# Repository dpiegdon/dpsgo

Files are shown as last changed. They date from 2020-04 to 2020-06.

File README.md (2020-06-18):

<!-- vim: tw=72 fo+=a
-->

DPSGO
=====

David's Pretty Satisfactory Gps-disciplined Oscillator

GPS disciplined oscillator
==========================

Accurate frequency reference for measurement equipment.

A 10MHz OCXO is tuned to a timing signal of a GPS, e.g. the 1PPS output.
A frequency syntheziser then generates different signals from this
reference as needed/configured by the user.

Development status
------------------

Currently I am working on the firmware for V1 of the PCB. During that I
found multiple issues with PCB-V1 (<a
href="https://github.com/dpiegdon/dpsgo/blob/master/pcb/export/PCB-v1.pdf">Schematic</a>)
which hopefully culminate in another revision of the PCB, and then the
firmware. See <a
href="https://github.com/dpiegdon/dpsgo/blob/master/pcb/export/PCB-v1.ERRATA">PCB-V1
ERRATA</a>.

I.e.: usable, but only as a prototype development platform for V2.

The main control loop (OCXO -> frequency comparison -> DAC) works and
the OCXO can be tuned to the GPS signal within 1PPB or better.

The chosen *tiny* FPGA is too small to hold all the logic that was
designated for it. Most LEDs are connected to it and cannot be addressed
because of that. Currently also the rotary encoder and buttons are
connected to it and are usable, but may be removed to have more logic
for frequency adjustment. In PCB-V2 I will likely move the UI to the
microcontroller, or pick a slightly larger FPGA, e.g. the HX1K.

System components PCB-V1
------------------------

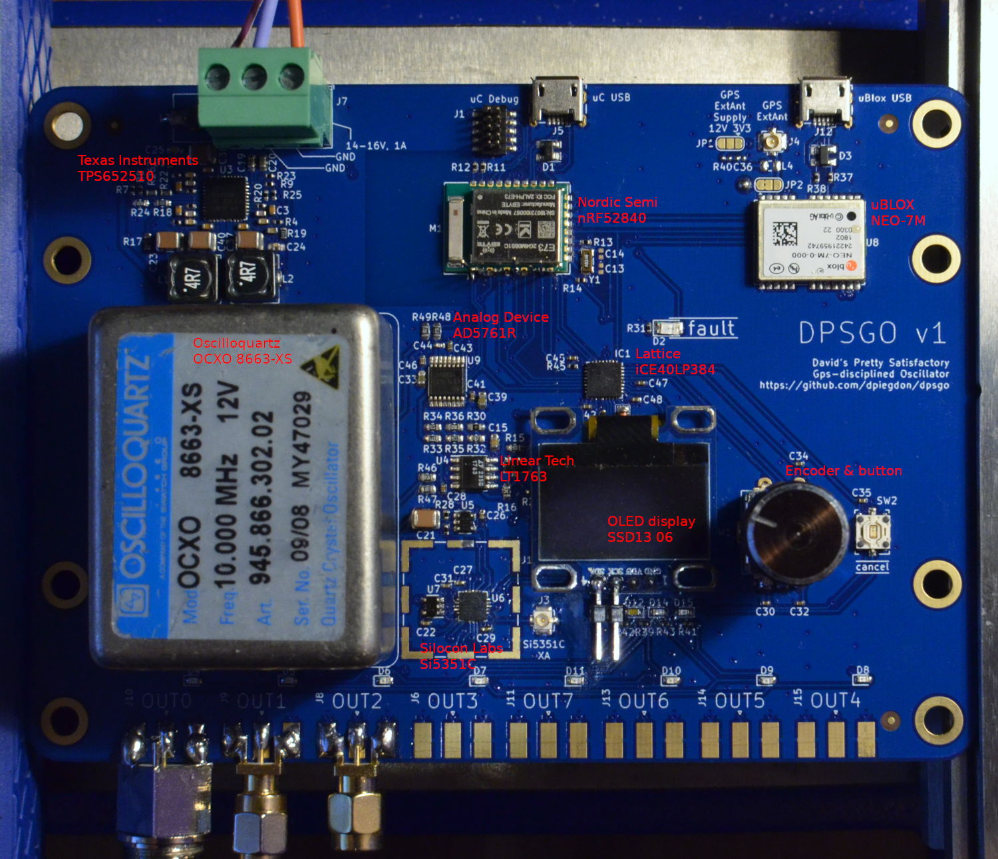
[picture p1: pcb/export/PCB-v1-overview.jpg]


<a
href="https://github.com/dpiegdon/dpsgo/blob/master/pcb/export/PCB-v1.pdf">Schematic.</a>

OCXO: refurbished 8663-XS with 10MHz output

DAC: AD5761R 16bit high quality low speed DAC with internal reference,
generates tuning signal for OCXO

GPS: uBlox NEO 7M module with 1PPS output

VCXO: Si5351-C frequency generator for programmable output frequencies

 * CLK0: 90MHz as input for frequency comparison in the FPGA (for
   automatic tuning)

 * CLK1: 10MHz reference output signal

 * other programmable outputs (currently disabled)

FPGA: Lattice LP384: measures difference between the generated reference
output and the GPS reference signal. That information is used to
calculate the tuning voltage for the OCXO.

uC: nRF52840 as system- and display-controller

Power input: 14-16V

PMIC: TPS652510 PMIC generating three rails of:

 * 12V: OCXO

 * 3.3V: digital logic

 * 1.2V: FPGA core voltage

Additional LDO for:

 * 10V: DAC output rail (from 12V rail)

Temperature sensors: MCP9808 under OCXO and on bottom-side of PMIC (not
visible in photo).

User interface:

 * SSD1306

 * Rotary encoder and buttons (via FPGA)

 * LEDs (currently not addressalbe as FPGA cannot hold more logic)

Interfaces:

 * USB to both GPS receiver and microcontroller

 * potentially Bluetooth or 802.11.5 to microcontroller

 * JTAG/SWD to microcontroller

External references
-------------------

A list of some hobby GPSDO designs:
https://attila.kinali.ch/blog/2016/02/07/gps-disciplined-oscillator

A GPSDO with rubidium standard:
http://www.medpants.com/my-reeds/itemlist/category/28-electronics

Alternative OCXO tuning schematic:
https://gerrysweeney.com/wp-content/uploads/2013/10/OCXO-Rev-1F.png

"bt7tbl" GPSDO that can be bought on the internets:
https://www.eevblog.com/forum/testgear/bg7tbl-gpsdo-master-reference/

Single-chip GPSDO control loop GPSDO:
https://www.analog.com/media/en/technical-documentation/application-notes/AN-1002.pdf

"OpenPPS" GPSDO project:
http://www.rocketmanrc.com/openpps.html

"Themis" GPSDO from HPSDR:
http://openhpsdr.org/wiki/index.php?title=GPSTCXO

GPSDO by dfannin:
https://github.com/dfannin/gpsdo

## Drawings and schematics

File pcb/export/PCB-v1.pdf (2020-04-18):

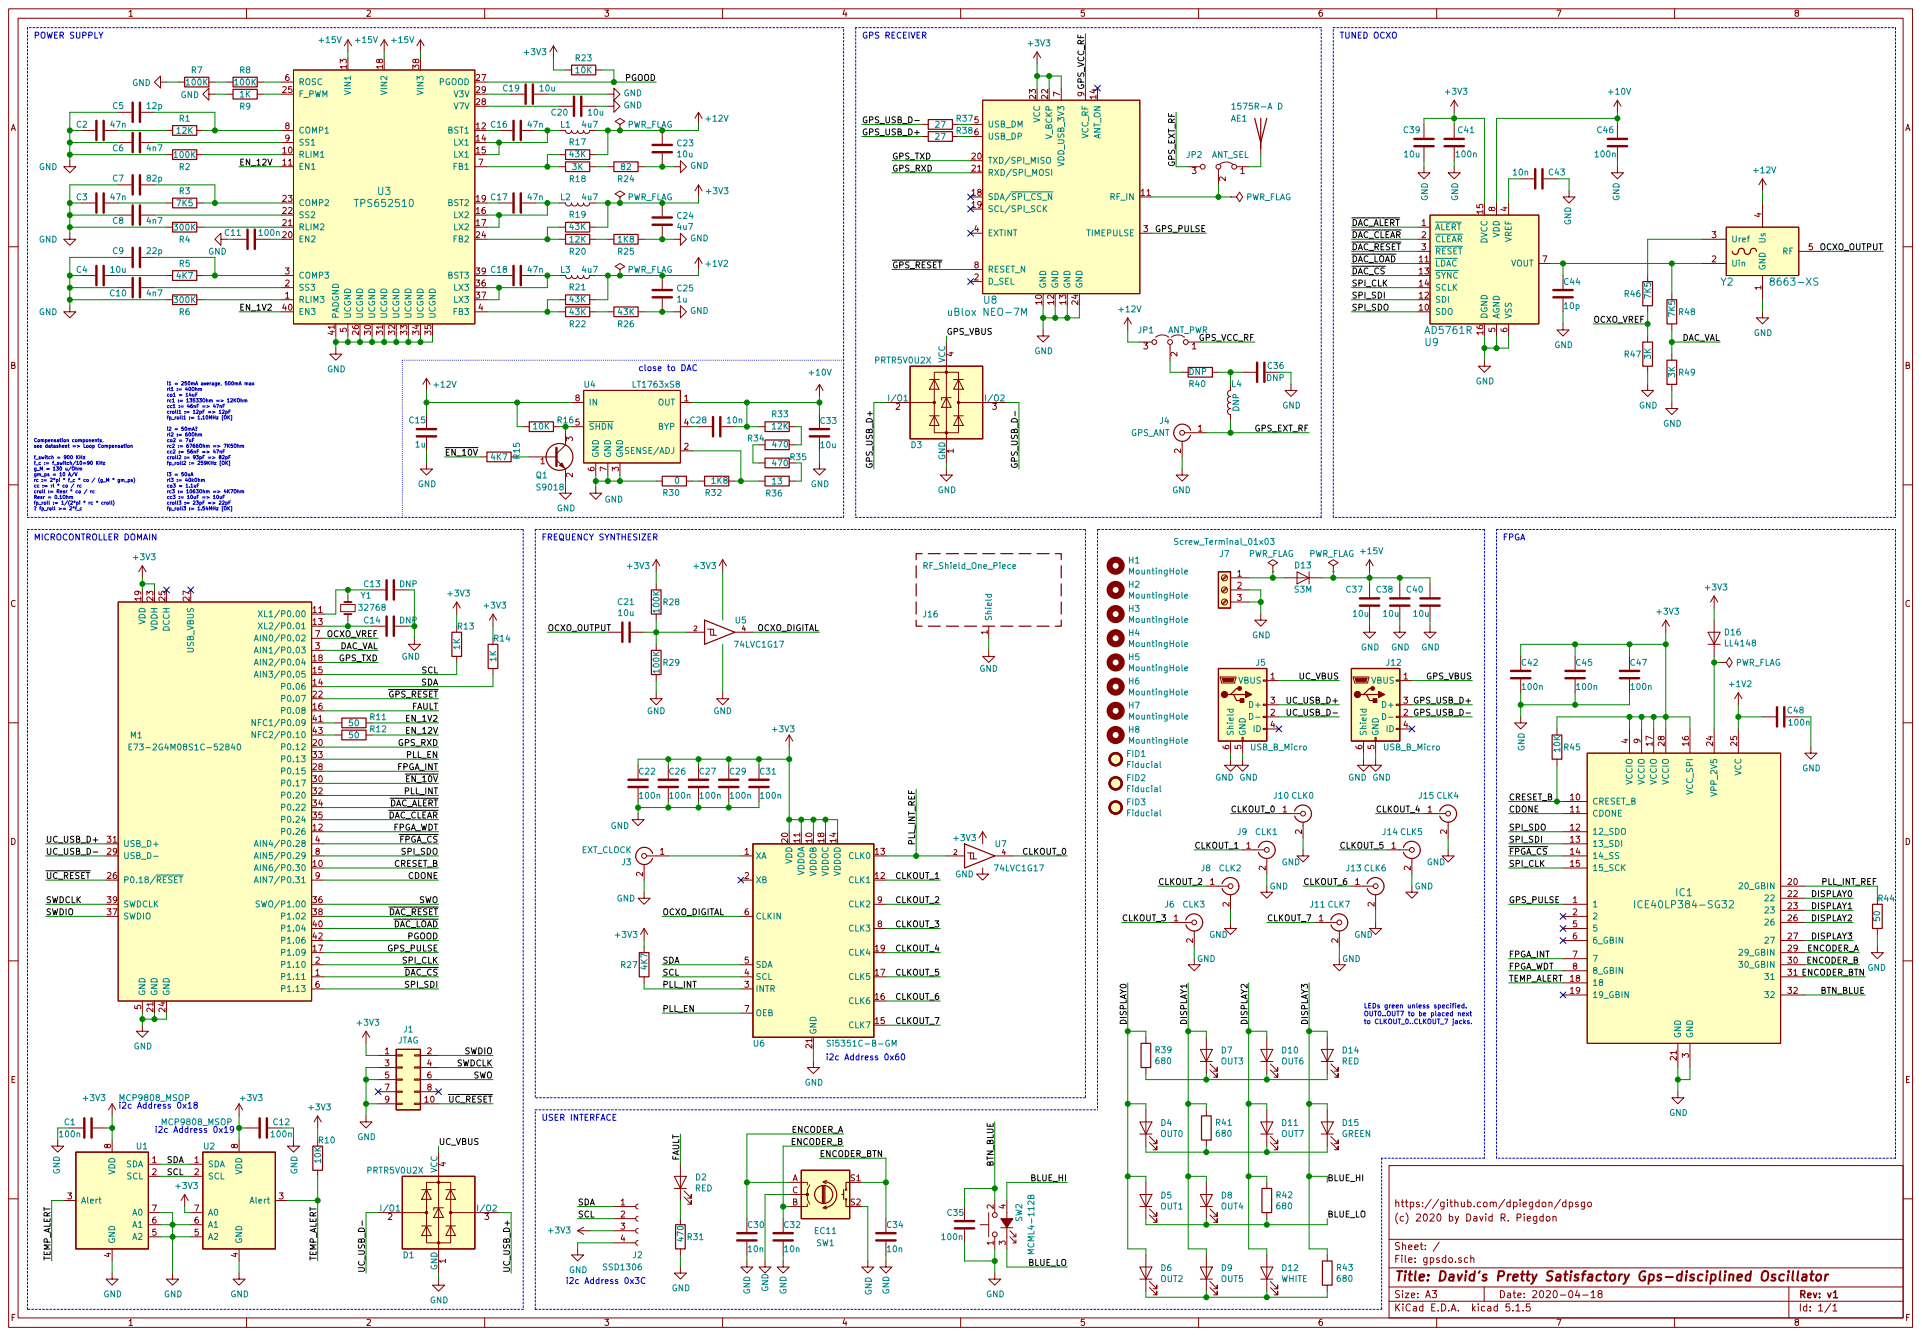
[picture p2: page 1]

Compensation components, see datasheet => Loop Compensation

croll := Resr * co / rc Resr = 0.1Ohm

FID3 Fiducial FID2 Fiducial FID1 Fiducial GNDShield

BLUE_HI LEDs green unless specified. OUT0..OUT7 to be placed next

https://github.com/dpiegdon/dpsgo
File: gpsdo.sch Sheet: / (c) 2020 by David R. Piegdon

Id: 1/1 Title: David's Pretty Satisfactory Gps-disciplined Oscillator

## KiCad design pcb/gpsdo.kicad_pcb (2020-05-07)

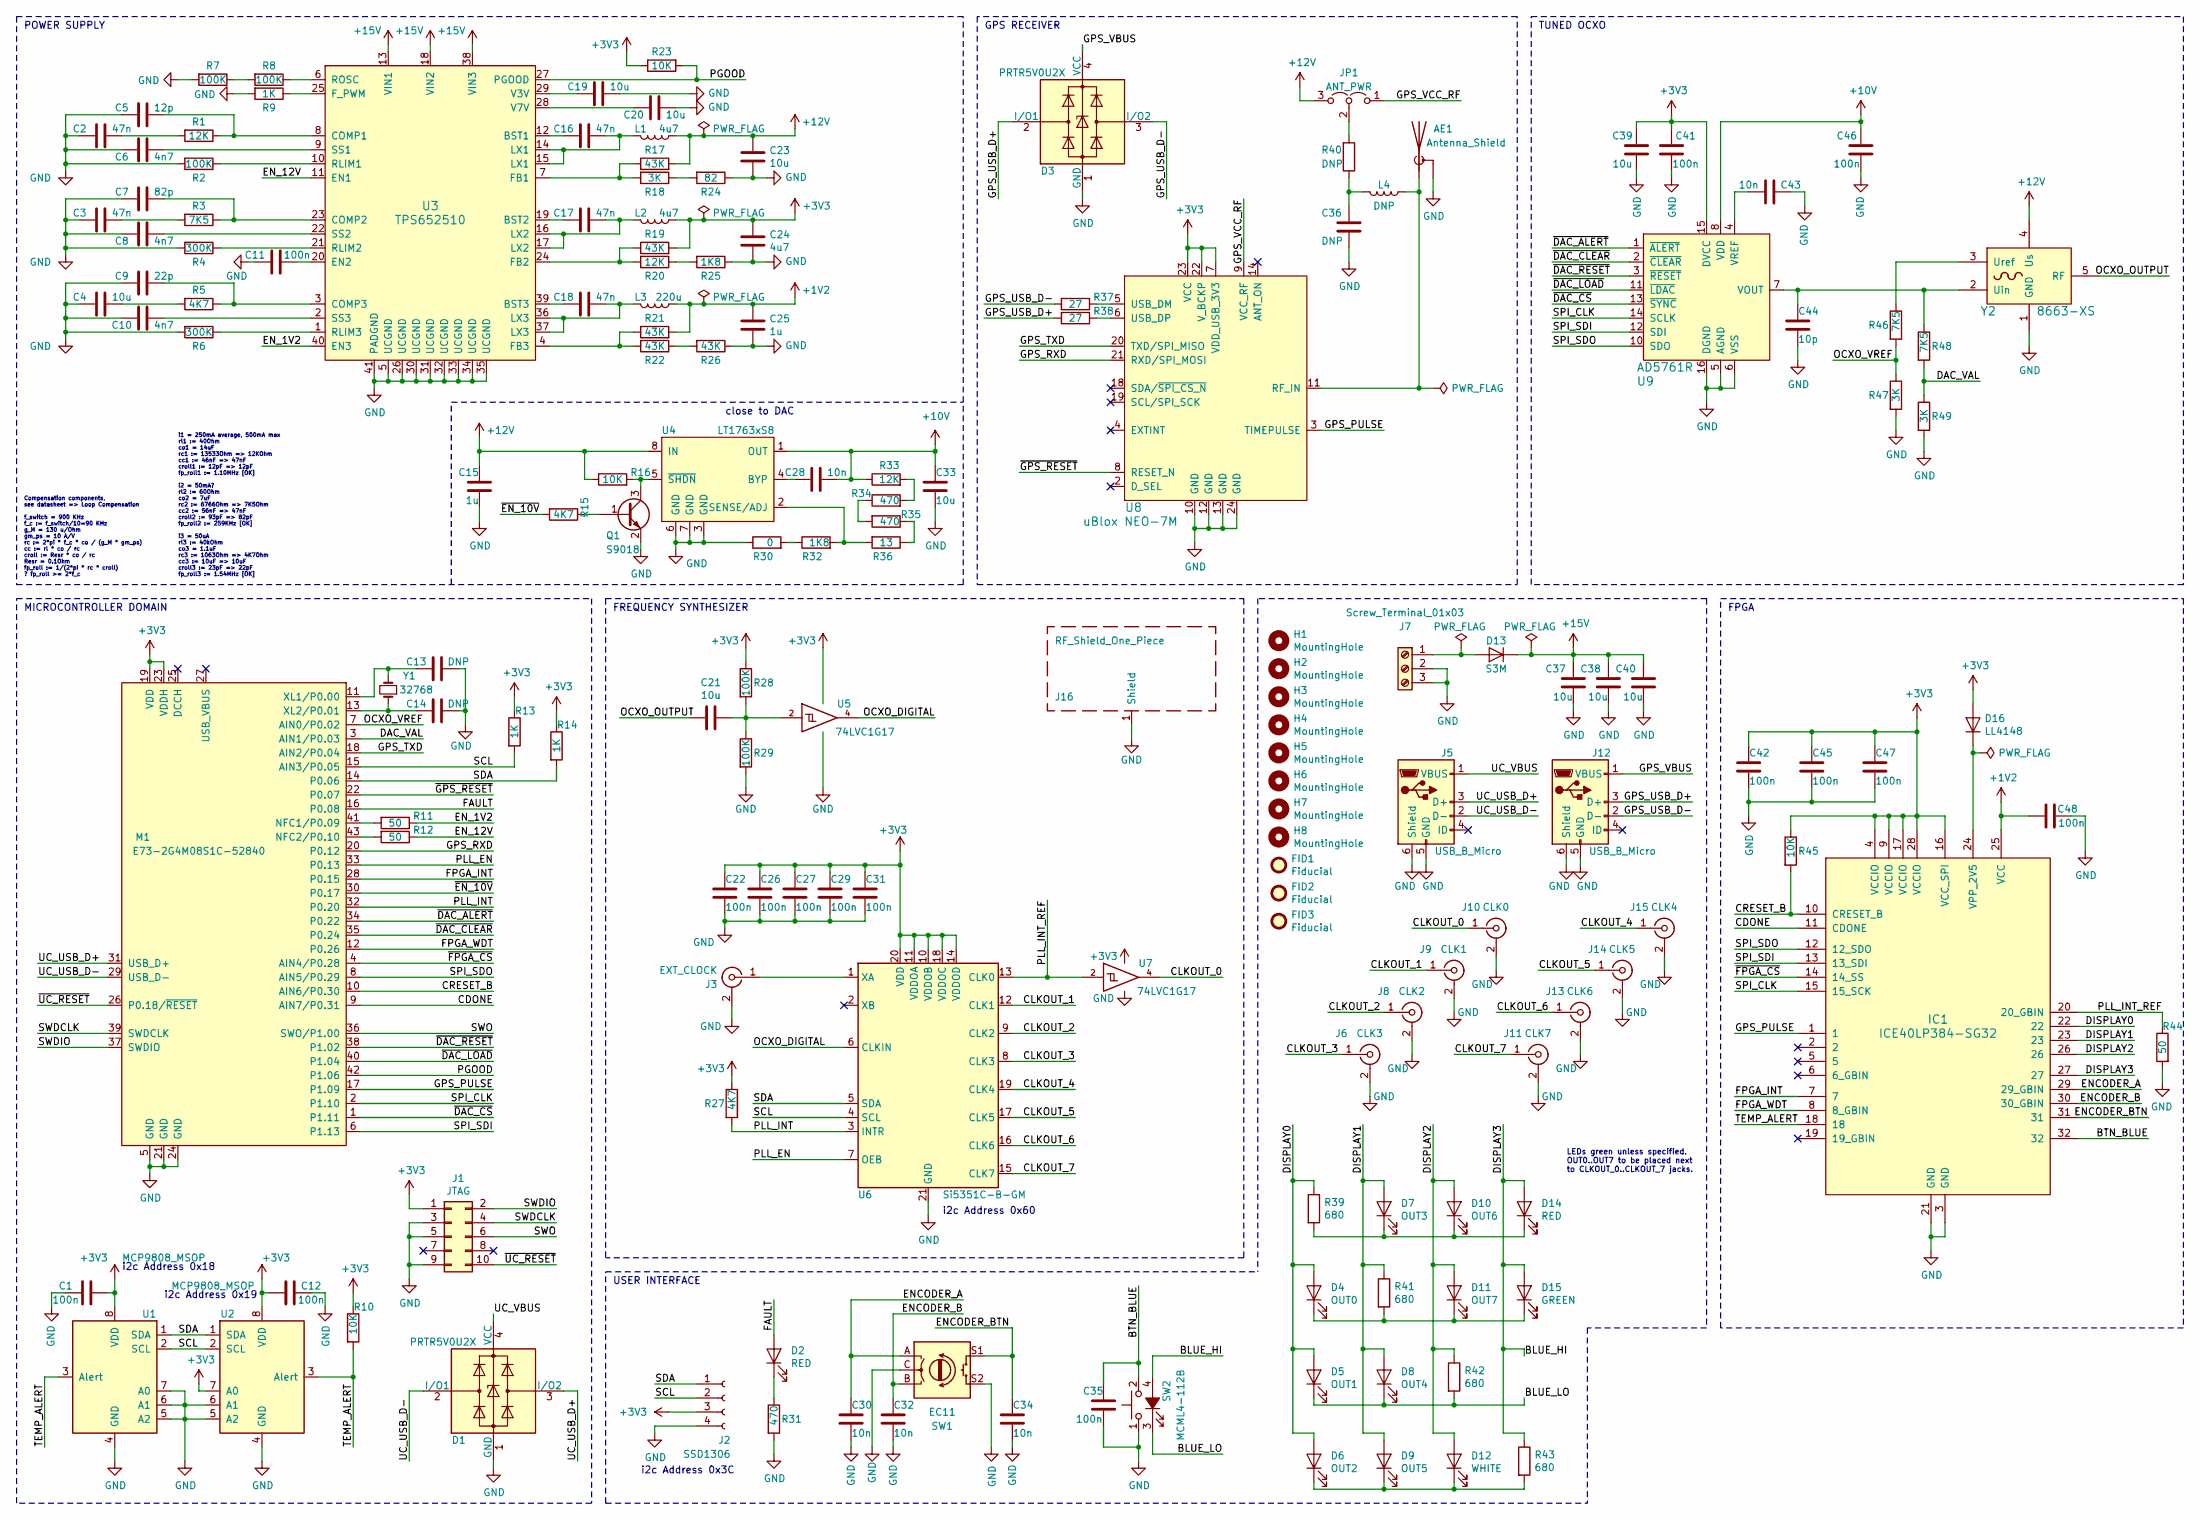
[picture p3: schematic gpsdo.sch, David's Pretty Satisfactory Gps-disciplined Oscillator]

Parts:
AE1: Antenna_Shield; Antenna-GPS-1575R
C1, C11, C12, C22, C26, C27, C29, C31, C35, C41, C42, C45, C46, C47, C48: 100n; C_0402_1005Metric
C2, C3, C16, C17, C18: 47n; C_0402_1005Metric
C4: 10u; C_0402_1005Metric
C5: 12p; C_0402_1005Metric
C6, C8, C10: 4n7; C_0402_1005Metric
C7: 82p; C_0402_1005Metric
C9: 22p; C_0402_1005Metric
C13, C14, C36: DNP; C_0402_1005Metric
C15, C25: 1u; C_0603_1608Metric
C19, C20, C33, C39: 10u; C_0603_1608Metric
C21, C23, C37, C38, C40: 10u; C_1210_3225Metric
C24: 4u7; C_0603_1608Metric
C28, C30, C32, C34, C43: 10n; C_0402_1005Metric
C44: 10p; C_0402_1005Metric
D1, D3: PRTR5V0U2X; SOT-143
D2: RED; D_1206_3216Metric
D4: OUT0; D_0603_1608Metric
D5: OUT1; D_0603_1608Metric
D6: OUT2; D_0603_1608Metric
D7: OUT3; D_0603_1608Metric
D8: OUT4; D_0603_1608Metric
D9: OUT5; D_0603_1608Metric
D10: OUT6; D_0603_1608Metric
D11: OUT7; D_0603_1608Metric
D12: WHITE; D_0603_1608Metric
D13: S3M; D_2010_5025Metric
D14: RED; D_0603_1608Metric
D15: GREEN; D_0603_1608Metric
D16: LL4148; D_MiniMELF
FID1, FID2, FID3: Fiducial; Fiducial_1mm_Mask3mm
H1, H2, H3, H4, H5, H6, H7, H8: MountingHole; MountingHole_4.3mm_M4_ISO14580_Pad
IC1: ICE40LP384-SG32; QFN-32-1EP_5x5mm_P0.5mm_EP3.6x3.6mm
J1: JTAG; PinHeader_2x05_P1.27mm_Vertical_SMD
J2: SSD1306; PinHeader_1x04_P2.54mm_Vertical
J3: EXT_CLOCK; U.FL_Molex_MCRF_73412-0110_Vertical
J5, J12: USB_B_Micro; USB_Micro-B_Aliexpress_7.2mm_Pitch
J6: CLK3; SMA_Molex_73251-1153_EdgeMount_Horizontal
J7: Screw_Terminal_01x03; TerminalBlock_Phoenix_PT-1,5-3-5.0-H_1x03_P5.00mm_Horizontal
J8: CLK2; SMA_Molex_73251-1153_EdgeMount_Horizontal
J9: CLK1; SMA_Molex_73251-1153_EdgeMount_Horizontal
J10: CLK0; SMA_Molex_73251-1153_EdgeMount_Horizontal
J11: CLK7; SMA_Molex_73251-1153_EdgeMount_Horizontal
J13: CLK6; SMA_Molex_73251-1153_EdgeMount_Horizontal
J14: CLK5; SMA_Molex_73251-1153_EdgeMount_Horizontal
J15: CLK4; SMA_Molex_73251-1153_EdgeMount_Horizontal
J16: RF_Shield_One_Piece; Laird_Technologies_BMI-S-202-F_16.50x16.50mm
JP1: ANT_PWR; SolderJumper-3_P1.3mm_Open_RoundedPad1.0x1.5mm
L1, L2: 4u7; L_7.3x7.3_H4.5
L3: 220u; L_Vishay_IHLP-1616
L4: DNP; L_0805_2012Metric
M1: E73-2G4M08S1C-52840; E73-2G4M80S1C
Q1: S9018; SOT-23
R1, R20: 12K; R_0402_1005Metric
R2, R7, R8, R28, R29: 100K; R_0402_1005Metric
R3: 7K5; R_0402_1005Metric
R4, R6: 300K; R_0402_1005Metric
R5, R27: 4K7; R_0402_1005Metric
R9, R13, R14: 1K; R_0402_1005Metric
R10, R23, R45: 10K; R_0402_1005Metric
R11, R12, R44: 50; R_0402_1005Metric
R15: 4K7; R_0603_1608Metric
R16: 10K; R_0603_1608Metric
R17: 43K; R_0603_1608Metric
R18, R47, R49: 3K; R_0603_1608Metric
R19, R21, R22, R26: 43K; R_0402_1005Metric
R24: 82; R_0603_1608Metric
R25: 1K8; R_0402_1005Metric
R30: 0; R_0603_1608Metric
R31: 470; R_0402_1005Metric
R32: 1K8; R_0603_1608Metric
R33: 12K; R_0603_1608Metric
R34, R35: 470; R_0603_1608Metric
R36: 13; R_0603_1608Metric
R37, R38: 27; R_0402_1005Metric
R39, R41, R42, R43: 680; R_0402_1005Metric
R40: DNP; R_0402_1005Metric
R46, R48: 7K5; R_0603_1608Metric
SW1: EC11; RotaryEncoder_Alps_EC11E-Switch_Vertical_H20mm
SW2: MCML4-112B; MCML4-L
U1, U2: MCP9808_MSOP; MSOP-8_3x3mm_P0.65mm
U3: TPS652510; QFN-40-1EP_6x6mm_P0.5mm_EP4.6x4.6mm_ThermalVias
U4: LT1763xS8; SO-8_3.9x4.9mm_P1.27mm
U5, U7: 74LVC1G17; SOT-23-5
U6: Si5351C-B-GM; QFN-20-1EP_4x4mm_P0.5mm_EP2.7x2.7mm
U8: uBlox NEO-7M; ublox_NEO_fixed_23
U9: AD5761R; TSSOP-16_4.4x5mm_P0.65mm
Y1: 32768; Crystal_SMD_3215-2Pin_3.2x1.5mm
Y2: 8663-XS; OCXO-8662-8663

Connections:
+1V2: C25.1, C48.1, IC1.25 (VCC), L3.1, R21.2
+3V3: C1.2, C12.2, C22.1, C24.1, C26.1, C27.1, C29.1, C31.1, C39.2, C41.2, C42.1, C45.1, C47.1, D16.2 (A), IC1.4 (VCCIO), IC1.9 (VCCIO), IC1.16 (VCC_SPI), IC1.17 (VCCIO), IC1.28 (VCCIO), J1.1, J2.3, L2.1, M1.19 (VDD), M1.23 (VDDH), R10.1, R13.1, R14.1, R19.2, R23.1, R27.1, R28.1, R45.1, U1.8 (VDD), U2.7 (A0), U2.8 (VDD), U5.5 (VCC), U6.10 (VDDOB), U6.11 (VDDOA), U6.14 (VDDOD), U6.18 (VDDOC), U6.20 (VDD), U7.5 (VCC), U8.7 (VDD_USB_3V3), U8.22 (V_BCKP), U8.23 (VCC), U9.15 (DVCC)
+10V: C28.2, C33.1, C46.2, R33.1, U4.1 (OUT), U9.8 (VDD)
+12V: C15.2, C23.1, JP1.3 (B), L1.1, R16.1, R17.2, U4.8 (IN), Y2.4 (Us)
+15V: C37.2, C38.2, C40.2, D13.1 (K), U3.13 (VIN1), U3.18 (VIN2), U3.38 (VIN3)
/BLUE_HI: D14.2 (A), D15.2 (A), IC1.27, R43.1, SW2.4 (A)
/BLUE_LO: D5.1 (K), D8.1 (K), R42.2, SW2.3 (K)
/BTN_BLUE: C35.1, IC1.32, SW2.2
/CDONE: IC1.11 (CDONE), M1.9 (AIN7/P0.31)
/CLKOUT_0: J10.1 (In), U7.4
/CLKOUT_1: J9.1 (In), U6.12 (CLK1)
/CLKOUT_2: J8.1 (In), U6.9 (CLK2)
/CLKOUT_3: J6.1 (In), U6.8 (CLK3)
/CLKOUT_4: J15.1 (In), U6.19 (CLK4)
/CLKOUT_5: J14.1 (In), U6.17 (CLK5)
/CLKOUT_6: J13.1 (In), U6.16 (CLK6)
/CLKOUT_7: J11.1 (In), U6.15 (CLK7)
/CRESET_B: IC1.10 (CRESET_B), M1.10 (AIN6/P0.30), R45.2
/DAC_VAL: M1.3 (AIN1/P0.03), R48.2, R49.1
/DISPLAY0: D4.2 (A), D5.2 (A), D6.2 (A), IC1.22, R39.1
/DISPLAY1: D7.2 (A), D8.2 (A), D9.2 (A), IC1.23, R41.1
/DISPLAY2: D10.2 (A), D11.2 (A), D12.2 (A), IC1.26, R42.1
/ENCODER_A: C30.1, IC1.29 (29_GBIN), SW1.A
/ENCODER_B: C32.1, IC1.30 (30_GBIN), SW1.B
/ENCODER_BTN: C34.1, IC1.31, SW1.S1
/EN_1V2: R11.1, U3.40 (EN3)
/EN_12V: R12.1, U3.11 (EN1)
/FAULT: D2.2 (A), M1.16 (P0.08)
/FPGA_INT: IC1.7, M1.28 (P0.15)
/FPGA_WDT: IC1.8 (8_GBIN), M1.12 (P0.26)
/GPS_PULSE: IC1.1, M1.17 (P1.09), U8.3 (TIMEPULSE)
/GPS_RXD: M1.20 (P0.12), U8.21 (RXD/SPI_MOSI)
/GPS_TXD: M1.18 (AIN2/P0.04), U8.20 (TXD/SPI_MISO)
/GPS_USB_D+: D3.2 (I/O1), J12.3 (D+), R38.2
/GPS_USB_D-: D3.3 (I/O2), J12.2 (D-), R37.2
/GPS_VBUS: D3.4 (VCC), J12.1 (VBUS)
/GPS_VCC_RF: JP1.1 (A), U8.9 (VCC_RF)
/OCXO_DIGITAL: U5.4, U6.6 (CLKIN)
/OCXO_OUTPUT: C21.2, Y2.5 (RF)
/OCXO_VREF: M1.7 (AIN0/P0.02), R46.2, R47.1
/PGOOD: M1.42 (P1.06), R23.2, U3.27 (PGOOD)
/PLL_EN: M1.33 (P0.13), U6.7 (OEB)
/PLL_INT: M1.32 (P0.20), R27.2, U6.3 (INTR)
/PLL_INT_REF: IC1.20 (20_GBIN), R44.1, U6.13 (CLK0), U7.2
/SCL: J2.2, M1.15 (AIN3/P0.05), R13.2, U1.2 (SCL), U2.2 (SCL), U6.4 (SCL)
/SDA: J2.1, M1.14 (P0.06), R14.2, U1.1 (SDA), U2.1 (SDA), U6.5 (SDA)
/SPI_CLK: IC1.15 (15_SCK), M1.2 (P1.10), U9.14 (SCLK)
/SPI_SDI: IC1.13 (13_SDI), M1.6 (P1.13), U9.12 (SDI)
/SPI_SDO: IC1.12 (12_SDO), M1.8 (AIN5/P0.29), U9.10 (SDO)
/SWDCLK: J1.4, M1.39 (SWDCLK)
/SWDIO: J1.2, M1.37 (SWDIO)
/SWO: J1.6, M1.36 (SWO/P1.00)
/TEMP_ALERT: IC1.18, R10.2, U1.3 (Alert), U2.3 (Alert)
/UC_USB_D+: D1.3 (I/O2), J5.3 (D+), M1.31 (USB_D+)
/UC_USB_D-: D1.2 (I/O1), J5.2 (D-), M1.29 (USB_D-)
/UC_VBUS: D1.4 (VCC), J5.1 (VBUS)
/~DAC_ALERT: M1.34 (P0.22), U9.1 (~ALERT)
/~DAC_CLEAR: M1.35 (P0.24), U9.2 (~CLEAR)
/~DAC_CS: M1.1 (P1.11), U9.13 (~SYNC)
/~DAC_LOAD: M1.40 (P1.04), U9.11 (~LDAC)
/~DAC_RESET: M1.38 (P1.02), U9.3 (~RESET)
/~EN_10V: M1.30 (P0.17), R15.2
/~FPGA_CS: IC1.14 (14_SS), M1.4 (AIN4/P0.28)
/~GPS_RESET: M1.22 (P0.07), U8.8 (RESET_N)
/~UC_RESET: J1.10, M1.26 (P0.18/~RESET)
GND: AE1.2 (Shield), C1.1, C2.2, C3.2, C4.2, C5.1, C6.1, C7.1, C8.1, C9.1, C10.1, C11.1, C12.1, C13.1, C14.1, C15.1, C19.1, C20.1, C22.2, C23.2, C24.2, C25.2, C26.2, C27.2, C29.2, C30.2, C31.2, C32.2, C33.2, C34.2, C35.2, C36.2, C37.1, C38.1, C39.1, C40.1, C41.1, C42.2, C43.2, C44.2, C45.2, C46.1, C47.2, C48.2, D1.1 (GND), D3.1 (GND), IC1.3 (GND), IC1.21 (GND), J1.3, J1.5, J1.9, J2.4, J3.2 (Ext), J5.5 (GND), J5.6 (Shield), J6.2 (Ext), J7.2, J7.3, J8.2 (Ext), J9.2 (Ext), J10.2 (Ext), J11.2 (Ext), J12.5 (GND), J12.6 (Shield), J13.2 (Ext), J14.2 (Ext), J15.2 (Ext), J16.1, M1.5 (GND), M1.21 (GND), M1.24 (GND), Q1.2 (E), R2.2, R4.2, R6.2, R7.2, R9.2, R24.1, R25.1, R26.1, R29.2, R30.1, R31.2, R44.2, R47.2, R49.2, SW1.C, SW1.S2, SW2.1, U1.4 (GND), U1.5 (A2), U1.6 (A1), U1.7 (A0), U2.4 (GND), U2.5 (A2), U2.6 (A1), U3.5 (UCGND), U3.26 (UCGND), U3.30 (UCGND), U3.31 (UCGND), U3.32 (UCGND), U3.33 (UCGND), U3.34 (UCGND), U3.35 (UCGND), U3.41 (PADGND), U4.3 (GND), U4.6 (GND), U4.7 (GND), U5.3 (GND), U6.21 (GND), U7.3 (GND), U8.10 (GND), U8.12 (GND), U8.13 (GND), U8.24 (GND), U9.5 (AGND), U9.6 (VSS), U9.16 (DGND), Y2.1 (GND)
unnamed: AE1.1 (A), L4.1, U8.11 (RF_IN)
unnamed: C2.1, R1.2
unnamed: C3.1, R3.2
unnamed: C4.1, R5.2
unnamed: C5.2, R1.1, U3.8 (COMP1)
unnamed: C6.2, U3.9 (SS1)
unnamed: C7.2, R3.1, U3.23 (COMP2)
unnamed: C8.2, U3.22 (SS2)
unnamed: C9.2, R5.1, U3.3 (COMP3)
unnamed: C10.2, U3.2 (SS3)
unnamed: C11.2, U3.20 (EN2)
unnamed: C13.2, M1.11 (XL1/P0.00), Y1.2
unnamed: C14.2, M1.13 (XL2/P0.01), Y1.1
unnamed: C16.1, L1.2, U3.14 (LX1), U3.15 (LX1)
unnamed: C16.2, U3.12 (BST1)
unnamed: C17.1, L2.2, U3.16 (LX2), U3.17 (LX2)
unnamed: C17.2, U3.19 (BST2)
unnamed: C18.1, L3.2, U3.36 (LX3), U3.37 (LX3)
unnamed: C18.2, U3.39 (BST3)
unnamed: C19.2, U3.29 (V3V)
unnamed: C20.2, U3.28 (V7V)
unnamed: C21.1, R28.2, R29.1, U5.2
unnamed: C28.1, U4.4 (BYP)
unnamed: C36.1, L4.2, R40.1
unnamed: C43.1, U9.4 (VREF)
unnamed: C44.1, R48.1, U9.7 (VOUT), Y2.2 (Uin)
unnamed: D2.1 (K), R31.1
unnamed: D7.1 (K), D10.1 (K), D14.1 (K), R39.2
unnamed: D4.1 (K), D11.1 (K), D15.1 (K), R41.2
unnamed: D6.1 (K), D9.1 (K), D12.1 (K), R43.2
unnamed: D13.2 (A), J7.1
unnamed: D16.1 (K), IC1.24 (VPP_2V5)
unnamed: J3.1 (In), U6.1 (XA)
unnamed: JP1.2 (C), R40.2
unnamed: M1.41 (NFC1/P0.09), R11.2
unnamed: M1.43 (NFC2/P0.10), R12.2
unnamed: Q1.1 (B), R15.1
unnamed: Q1.3 (C), R16.2, U4.5 (~SHDN)
unnamed: R2.1, U3.10 (RLIM1)
unnamed: R4.1, U3.21 (RLIM2)
unnamed: R6.1, U3.1 (RLIM3)
unnamed: R7.1, R8.2
unnamed: R8.1, U3.6 (ROSC)
unnamed: R9.1, U3.25 (F_PWM)
unnamed: R17.1, R18.2, U3.7 (FB1)
unnamed: R18.1, R24.2
unnamed: R19.1, R20.2, U3.24 (FB2)
unnamed: R20.1, R25.2
unnamed: R21.1, R22.2, U3.4 (FB3)
unnamed: R22.1, R26.2
unnamed: R30.2, R32.1
unnamed: R32.2, R36.2, U4.2 (SENSE/ADJ)
unnamed: R33.2, R34.2
unnamed: R34.1, R35.2
unnamed: R35.1, R36.1
unnamed: R37.1, U8.5 (USB_DM)
unnamed: R38.1, U8.6 (USB_DP)
unnamed: R46.1, Y2.3 (Uref)

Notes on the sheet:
POWER SUPPLY
GPS RECEIVER
MICROCONTROLLER DOMAIN
TUNED OCXO
FREQUENCY SYNTHESIZER
FPGA
USER INTERFACE
close to DAC
i1 = 250mA average, 500mA max rl1 := 40Ohm co1 = 14uF rc1 := 13533Ohm => 12KOhm cc1 := 46nF => 47nF croll1 := 12pF => 12pF fp_roll1 := 1.10MHz [OK] i2 = 50mA? rl2 := 60Ohm co2 = 7uF rc2 := 6766Ohm => 7K5Ohm cc2 := 56nF => 47nF croll2 := 93pF => 82pF fp_roll2 := 259KHz [OK] i3 = 50uA rl3 := 40kOhm c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
Compensation components, see datasheet => Loop Compensation f_switch = 900 KHz f_c := f_switch/10=90 KHz g_M = 130 u/Ohm gm_ps = 10 A/V rc := 2*pi * f_c * co / (g_M * gm_ps) cc := rl * co / rc croll := Resr * co / rc Resr = 0.1Ohm fp_roll := 1/(2*pi * rc * croll) ? fp_roll >= 2*f_c
LEDs green unless specified. OUT0..OUT7 to be placed next to CLKOUT_0..CLKOUT_7 jacks.
i2c Address 0x19
i2c Address 0x3C
i2c Address 0x60
i2c Address 0x18

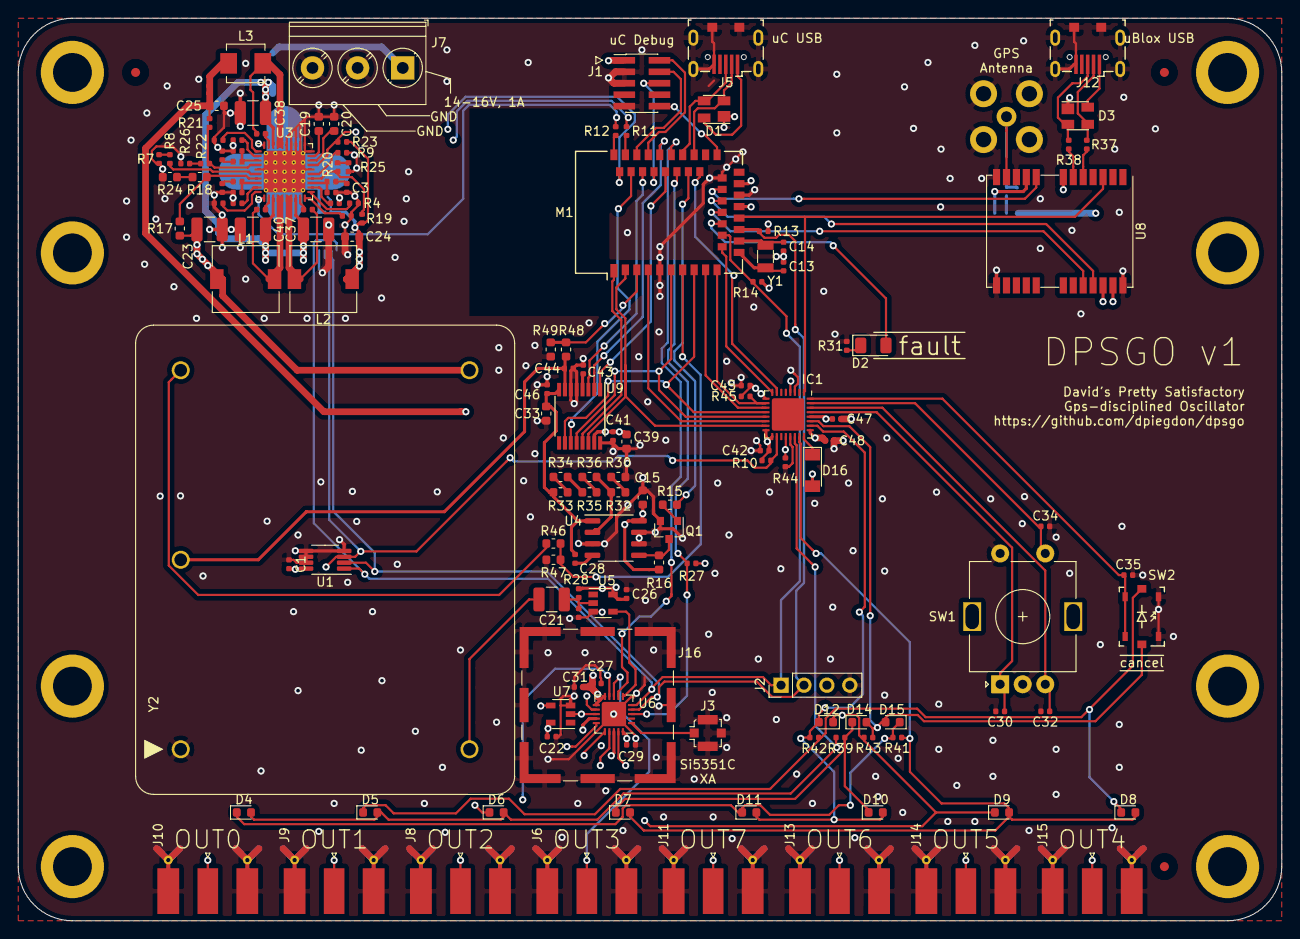
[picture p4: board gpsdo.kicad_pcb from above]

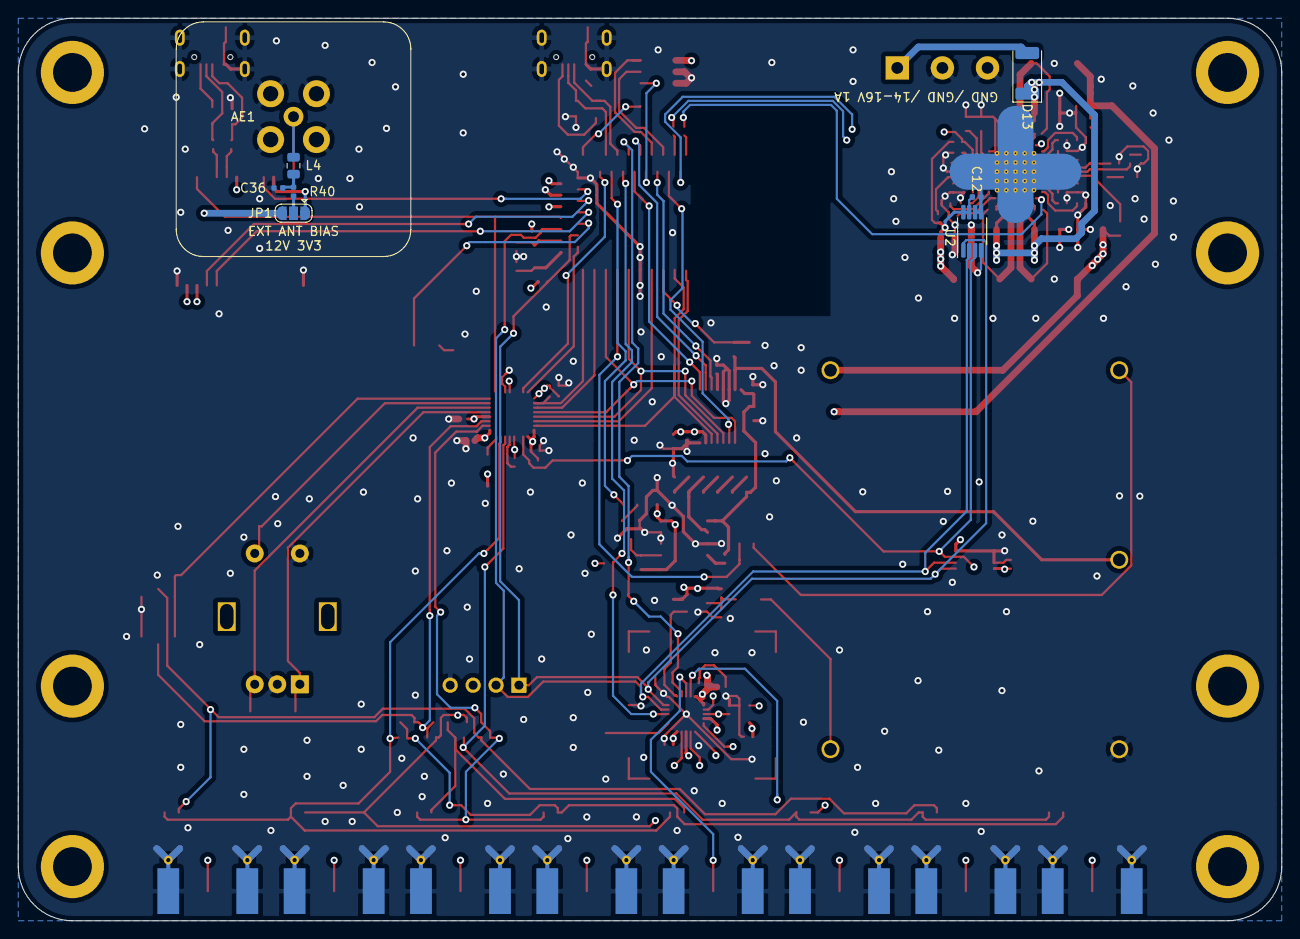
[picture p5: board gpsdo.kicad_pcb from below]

Board: 4 copper layers, 140.0 x 100.0 mm, 161 parts (8 on the bottom side), 124 nets.

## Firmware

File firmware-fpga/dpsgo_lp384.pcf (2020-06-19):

# SPI interface
set_io --warn-no-port SCK 15
set_io --warn-no-port SS 14
set_io --warn-no-port SDI 13
set_io --warn-no-port SDO 12
set_io --warn-no-port FPGA_INT 7
set_io --warn-no-port FPGA_WDT 8

# clocks
set_io --warn-no-port MAJOR_CLOCK 20
set_io --warn-no-port MINOR_CLOCK 1

# other IO
set_io --warn-no-port TEMP_ALERT 18

# buttons and encoder
set_io --warn-no-port ENCODER_A 29
set_io --warn-no-port ENCODER_B 30
set_io --warn-no-port ENCODER_BTN 31
set_io --warn-no-port BTN_BLUE 32

# LED matrix
set_io --warn-no-port LED_MATRIX[0] 22
set_io --warn-no-port LED_MATRIX[1] 23
set_io --warn-no-port LED_MATRIX[2] 26
set_io --warn-no-port LED_MATRIX[3] 27

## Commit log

2020-04-05 stub PCB files
    [gpsdo.kicad_pcb, gpsdo.sch]
2020-04-05 concept PCB
    [gpsdo.sch]
2020-04-05 add 8663-XS OCXO
    [gpsdo.sch]
2020-04-05 add ublox NEO-7 GPS module
    [gpsdo.sch]
2020-04-05 schematic progress, mark areas with TODOs
    [gpsdo.sch]
2020-04-06 add TPS652510, schematic progress and layout
    [gpsdo.sch]
2020-04-06 PCB progress
    [gpsdo.sch]
2020-04-06 schematic progress
    [gpsdo.sch]
2020-04-08 UI: rotary encoder would be nice, cleanup
    [gpsdo.sch]
2020-04-08 remove some errors and warnings
    [gpsdo.sch]
2020-04-09 power concepts; bias and digitze OCXO output
    [gpsdo.sch]
2020-04-10 power progress, cleanup
    [gpsdo.sch]
2020-04-10 LEDs, front/rear panel
    [gpsdo.sch]
2020-04-11 stub verilog implementation to see how much logic fits into the LP384 ; schematic adaptions for that
    [gpsdo.sch]
2020-04-11 FPGA progress, interface and schematic-cleanup
    [gpsdo.sch]
2020-04-11 partial footprint assignment
    [gpsdo.sch]
2020-04-12 footprints, GPS antenna optionally can be biased now
    [gpsdo.sch]
2020-04-12 review progress of schematic
    [gpsdo.sch]
2020-04-13 review footprints and more
    [gpsdo.sch]
2020-04-13 add current netlist
    [gpsdo.sch]
2020-04-13 first routing tests
    [gpsdo.kicad_pcb, gpsdo.sch]
2020-04-13 replace expensive Si7010 with two cheaper temp sensors
    [gpsdo.kicad_pcb, gpsdo.sch]
2020-04-13 remove PCB routing, restart from scratch
    [gpsdo.kicad_pcb]
2020-04-14 new routing
    [gpsdo.kicad_pcb]
2020-04-15 tps652510 routing, inductor footprint
    [gpsdo.kicad_pcb, gpsdo.sch]
2020-04-16 tps652510 routing
    [gpsdo.kicad_pcb]
2020-04-16 basic component placement and board layout
    [gpsdo.kicad_pcb, gpsdo.sch]
2020-04-17 pin assignment optimization, routing
    [gpsdo.kicad_pcb, gpsdo.sch]
2020-04-17 routing progress, silkscreen
    [gpsdo.kicad_pcb]
2020-04-17 more layout cleanup
    [gpsdo.kicad_pcb]
2020-04-17 add mounting holes, cleanup bord edge and mounting strategy. increase board size for that.
    [gpsdo.kicad_pcb, gpsdo.sch]
2020-04-17 added shield and more silkscreen, cleanup
    [gpsdo.kicad_pcb, gpsdo.sch]
2020-04-18 more routing cleanup
    [gpsdo.kicad_pcb]
2020-04-18 PCB v1
    more cleanup, release v1
    [gpsdo.kicad_pcb, gpsdo.sch]
2020-04-18 add schematic to PCB-v1 exports
2020-04-18 adapt FPGA pinout to PCB-v1
2020-04-18 add notes on PCB-v1 improvements
2020-04-20 fix missing PAD23 of ublox neo in paste layer (thanks to JLCPCB for spotting this!)
    [PCB-v1-F_Paste-FixedPad23.gbr, gpsdo.kicad_pcb, gpsdo.sch]
2020-04-30 add PCB V1 errata on power rail ripple
2020-04-30 fix L3 to decrease ripple on 1V2 rail
    [gpsdo.kicad_pcb, gpsdo.sch]
2020-05-01 added more ERRATA for the PCB
2020-05-02 more errata for PCB
2020-05-05 more PCB-v1 errata
2020-05-07 change GPS antenna to support either ceramic antenna or SMA with optional bias
    [gpsdo.kicad_pcb, gpsdo.sch]
2020-05-07 increase distance between input protection diode and GND pin of input connector
    [gpsdo.kicad_pcb]
2020-05-07 increase distance of DAC output rail to any noisy digital signal
    [gpsdo.kicad_pcb]
2020-05-07 increase visibility of pin1 of SWD connector.
    [gpsdo.kicad_pcb]
2020-05-21 add errata on R44 overloading CLK0 output with 50Ohm. reduce to 470Ohm
2020-05-22 current firmware status
2020-05-25 current firmware state
2020-05-28 use sensible display clock, default-on all LEDS for visual check
2020-05-30 PCB errata & documentation
2020-05-30 strip down FPGA design to fit into LP384: remove LEDs
2020-05-30 optimize FPGA timings and include temperature alert as input.
2020-05-30 more PCB errata
2020-06-05 current state + some documentation for public release
2020-06-05 add script to calculate improved values for power supply layout of TPS652510
